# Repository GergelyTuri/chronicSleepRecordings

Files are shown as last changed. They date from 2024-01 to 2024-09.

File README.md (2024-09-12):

# This repository contains hardware and software requirements for running continuous EEG/EMG recordings in mice.

We are developing a EEG/EMG setup to investigate the sleep profile and seizure
incidence in mice using Pinnacle Technology's [3-Channel EEG/EMG Mouse System](https://store.pinnaclet.com/products/8200-k1-3-channel-eeg-emg-mouse-system).

### Table of contents

| **Section** | **Description** |
|:-|:-|
| [Hardware](#hardware) | Hardware requirements and setup tutorial |
| [Software](#software) | Software requirements and setup tutorial |
| [Future directions](#future-directions) | Planned updates to the project |
| [Contact](#contact) | Email the researchers taking lead on the project |

## Hardware

The mouse EEG/EMG experiments take place inside modified Med Associates
sound-attenuating cubicles that are outfitted with
Faraday-shielding copper mesh and sound-proof acoustic foam panels. The
mice undergoing recordings are individually housed inside custom-cut acrylic cages.
Circadian lighting is achieved using LED & IR lights that are powered via
24-hour programmable outlet timers. EEG/EMG signals are recorded
using Pinnacle's EEG/EMG tethered mouse system and headmounts. Overhead cameras are used to record video of
mouse behavior in-sync with EEG/EMG recordings.

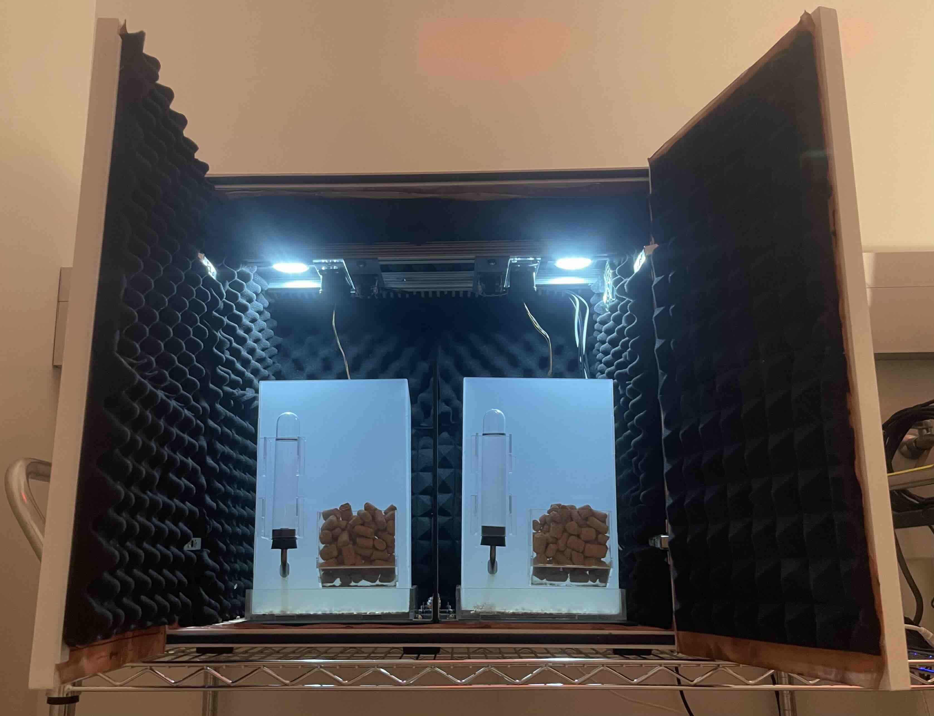
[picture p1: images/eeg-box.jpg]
EEG/EMG cubicle outfitted with copper mesh and acoustic foam panels

**Figure 1.** _Modified cubicle used for EEG/EMG recordings._

### Hardware requirements

- Pinnacle 3-Channel EEG/EMG Mouse System
- Pinnacle EEG/EMG headmounts
- Modified Med Associates Sound Attenuating Cubicle
- Recording enclosure
- Camera(s)
- Desktop/laptop (Windows OS)

### Hardware setup tutorial

For a detailed hardware setup tutorial, please click [here](./Hardware/).

## Software

We are using Pinnacle Technology's [Sirenia Acquisition Software](https://www.pinnaclet.com/sirenia.html) for video-EEG/EMG recordings, which requires the Windows OS environment.

For analysis, we are using [this MATLAB script found here](https://github.com/thepenglab/edfEEG2024) to analyze the sleep states from EEG/EMG data ('.edf' format).

### Software requirement

- [Sirenia Acquisition](https://www.pinnaclet.com/sirenia-download.html)
- [ffmpeg](https://www.gyan.dev/ffmpeg/builds/)
- [MATLAB script](https://github.com/thepenglab/edfEEG2024)
- Windows OS

### Software setup tutorial

For a detailed software setup tutorial, please click [here](./Software/).

## Future directions

1. Developing a software analysis guide
2. Developing a custom analysis code
3. Developing a DeepLabCut model for XY tracking

-----

## Contact

For any questions or inquiries, please email the researchers taking
lead on the project below:
- [Gergely Turi](mailto:gt2253@cumc.columbia.edu)
- [Rebecca Muhle](mailto:ram76@cumc.columbia.edu)
- [David Rivas](mailto:dfr5108@gmail.com)

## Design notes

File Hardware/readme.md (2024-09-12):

# Hardware 

## Hardware requirements

- Pinnacle 3-Channel EEG/EMG Mouse System
- Pinnacle EEG/EMG headmounts
- Modified Med Associates Sound Attenuating Cubicle
- Recording enclosure
- Camera(s)
- Desktop/laptop

## Bill of Materials

For a comprehensive list of hardware materials used in the build, please
click [here](./BOM.md).

## Laser-cut files

For the laser-cut files and drawings, please click [here](./Laser%20cut%20parts/).

## Setup guide

1. [Faraday-shielding and sound-proofing](./setup-guide/copper-foam.md)
2. [Aluminum framing](./setup-guide/aluminum-framing.md)
3. [Pinnacle System, lighting, & ventilation](./setup-guide/pinnacle-system.md)
4. [Camera setup](./setup-guide/camera-setup.md)
5. [Cable management](./setup-guide/cable-management.md)
6. [Recording enclosure](./setup-guide/recording-enclosure.md)
7. [Box divider](./setup-guide/box-divider.md)
8. [Connecting the EEG/EMG headmount](./setup-guide/headmount.md)

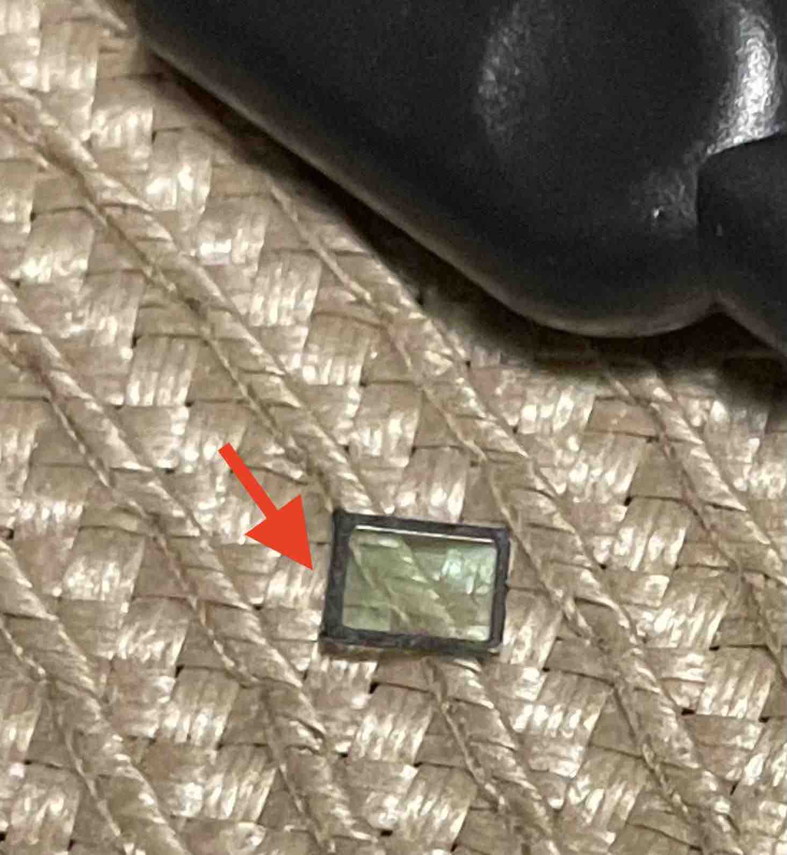
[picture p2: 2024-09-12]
images/logitech-ir-filter.jpg

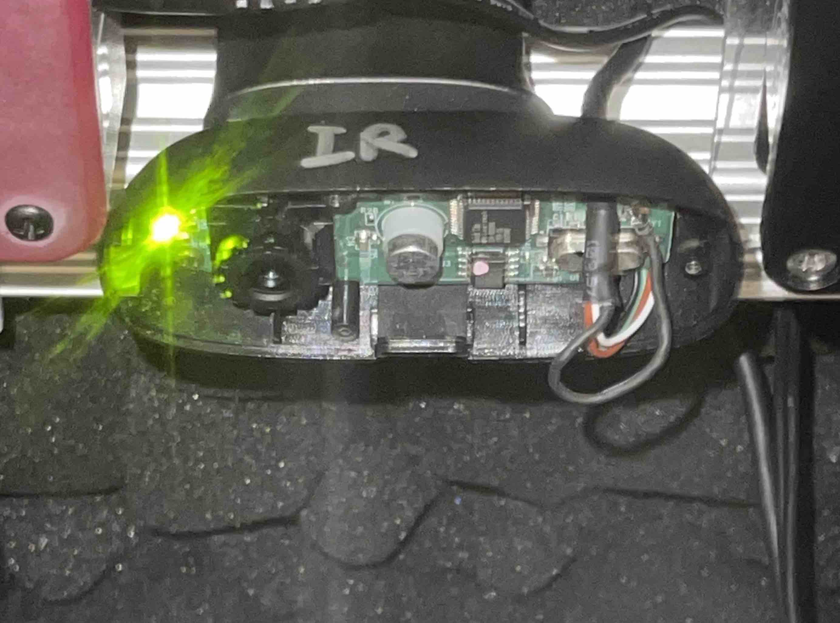
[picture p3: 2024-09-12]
images/logitech-c270.jpg

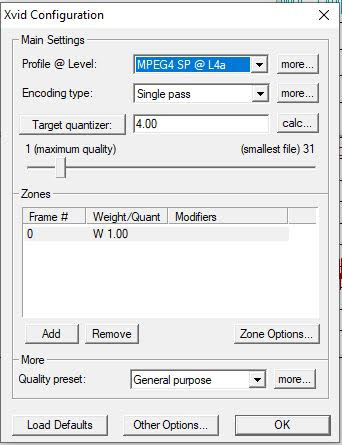
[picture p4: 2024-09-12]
images/xvid-config.jpg

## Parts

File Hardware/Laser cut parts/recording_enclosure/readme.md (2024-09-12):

# Recording enclosure files for laser cutting

The design of the enclosure is based on the Peng lab's*. A small modification has been made in the enclusure so there is no gap between the base and the top. At least two 18"x24", 1/8" thick Frosted Satin Ice acrilyc sheet is needed for the top of one enclosure. One sheet from the 1/4" acrylic is enough to make two bottoms.

* *The original Peng lab design allows the user for using the Peng lab's custom made treadmill for sleep deprivation (it has a gap betwen the bottom and the top).

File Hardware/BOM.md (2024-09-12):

# Bill of Materials

Comprehensive table of the hardware materials used in the build.

| Part name | Source | cat# | function | notes |
| -------- | -------- | -------- | -------- | -------- |
| 3-Channel EEG/EMG Mouse Data Conditioning and Acquisition System | Pinnacle Tech. | [8206-HR](https://store.pinnaclet.com/collections/3-channel-tethered-mouse-systems/products/8200-k1-3-channel-eeg-emg-mouse-system) | 2 EEG/ 1 EMG amplifier | |
| 3 channel mouse preamplifier | Pinnacle Tech. | [8202](https://store.pinnaclet.com/products/8202-3-channel-mouse-preamplifier) | Connects headmount to commutator | Custom length of 11.25 inches from connector to connector |
| 3-Channel Mouse Commutator and Swivel (6-pin) | Pinnacle Tech. | [8204-723](https://store.pinnaclet.com/products/8204-723-3-channel-mouse-commutator-and-swivel-6-pin) | Commutator ||
| 2 EEG/1 EMG Mouse Headmount | Pinnacle Tech. | [8201-SS](https://store.pinnaclet.com/products/8201-2-eeg-1-emg-mouse-headmount?variant=12390701727847) | EEG/EMG electrodes that connect to the 6-pin preamplifier | |
| 6 PIN Male to Male Cable (6 ft.) | Amazon | [B0933GL5CX](https://www.amazon.com/Shielded-Cable-Black-Mouse-Keyboard/dp/B0933GL5CX/) | Extension cable between 8206 amplifier and commutator |
| EEG/EMG Headmounts | Pinnacle Tech. | [8201-SS](https://store.pinnaclet.com/products/8201-2-eeg-1-emg-mouse-headmount?variant=12390701727847) | EEG/EMG signal probe | |
| Sound Attenuating Cubicle | Med Associates | [MDF](https://med-associates.com/product/sound-attenuating-cubicles-mdf/) | Cubicle enclosure | |
| Copper mesh (0.0045" diameter) | TWP | [100X100C0045](https://www.twpinc.com/100-mesh-copper-0045-wire-dia) | Faraday-shielding | Fixed using staples |
| Acoustic foam panels | Amazon | [B0BLTSW8KC](https://www.amazon.com/Self-Adhesive-Quick-Recovery-Elasticity-Eco-Friendly-WVOVW/dp/B0BLTSW8KC) | Sound-proofing | Fixed using staples |
| T-slot aluminum extrusion profile framing | 80/20 | [1010](https://8020.net/1010.html) | Mounting overhead accessories | Installed with 1/4" screws |
| Roll-in T-nuts | 80/20 | [3313](https://8020.net/3313.html) | Mounting overhead equipment to aluminum railing | |
| 10 & 15 Series Wiring Duct | 80/20 | [2899](https://8020.net/2899.html) | Cable management | Can alternatively use cable raceway |
| 1/8" & 1/4" acrylic sheets | Canalplastics | [various materials](https://www.canalplastic.com/) | material used for laser cutting | |
| Weld-on #4 glue | Amazon | [B00TCUJ7A8](https://www.amazon.com/Weldon-Applicator-Bottle-Pint-10308/dp/B00TCUJ7A8) | Adhere acrylic sheets | Applied with needle |
| Rat water bottle | WPI | [505432](https://www.wpiinc.com/var-505432-rat-mouse-water-bottle.html) | | |
| Arducam B0205 Camera | Amazon | [B0829HZ3Q7](https://www.amazon.com/Arducam-Computer-Automatic-Switching-All-Day/dp/B0829HZ3Q7/) | Video monitoring | |
| Dimmable LED lights | Amazon | [B0CCDPNYFG](https://www.amazon.com/JUSJUBR-Lighting-Dimmable-Function-Bookshelf/dp/B0CCDPNYFG) | Artificial daylight | |
| LED rotary dimmer switch | Amazon | [B07MM88SB6](https://www.amazon.com/TronicsPros-12V-24V-Dimmer-Switch-Controller/dp/B07MM88SB6) | Change LED light intensity | |
| IR light (optional) | Pinnacle Tech. | [9057](https://store.pinnaclet.com/products/9057-illuminator) | Night-time lighting | The Arducam B0205 camera already has automatic IR light bulbs |
| 24-HR programmable outlet timer | Amazon | [B07HCQKRRY](https://www.amazon.com/Fosmon-Programmable-Seasonal-Portable-Aquarium/dp/B07HCQKRRY) | Program circadian lighting | |
| 12V power sources | Amazon | N/A | powering multiple components | |
| 24V AC-to-DC power supply | Amazon | [B078RY7BPL](https://www.amazon.com/ALITOVE-Converter-Transformer-5-5x2-1mm-Computer/dp/B078RY7BPL) | Powering the cubicle fan | |

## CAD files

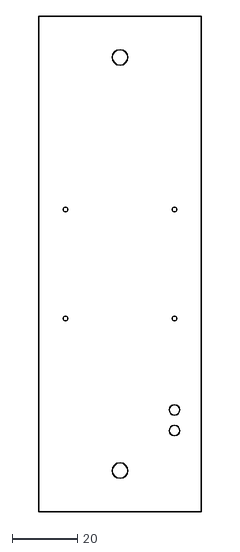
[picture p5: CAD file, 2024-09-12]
Hardware/Laser cut parts/arducam_mount/arducam_camera_mounting_plate.dxf
50.0 x 152.4

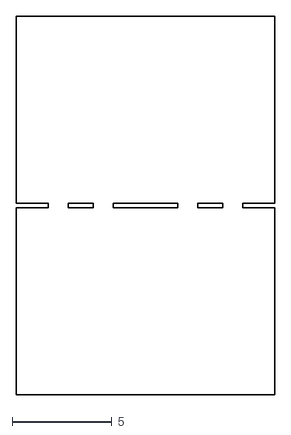
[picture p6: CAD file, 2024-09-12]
Hardware/Laser cut parts/box-divider/box-divider-pt2.dxf
13.0 x 19.0

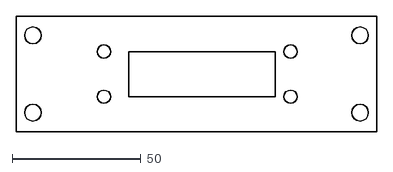
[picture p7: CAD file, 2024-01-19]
Hardware/Laser cut parts/commutator-holder/8206-commutator-holder/commuter holder GTs system.dxf
140.0 x 45.0

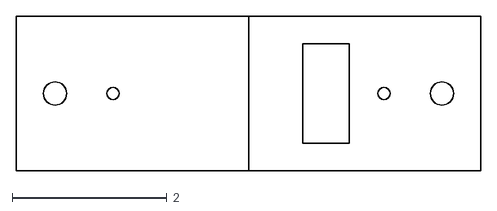
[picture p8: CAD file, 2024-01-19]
Hardware/Laser cut parts/commutator-holder/8401-commutator-holder/Commuter holder RMs system.dxf
6.00 x 2.00

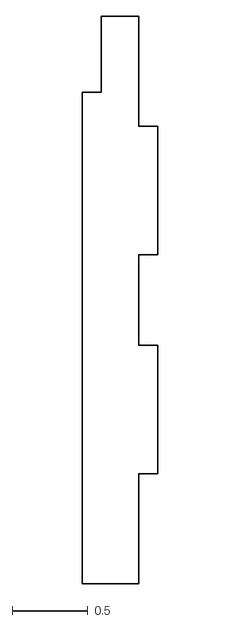
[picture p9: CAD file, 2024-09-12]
Hardware/Laser cut parts/fan-cover/fan-cover-pt2.dxf
0.5 x 3.75

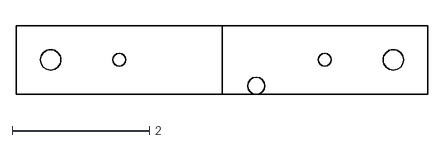
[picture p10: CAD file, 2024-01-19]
Hardware/Laser cut parts/ir_holder/IR_holder.dxf
6.00 x 1.01

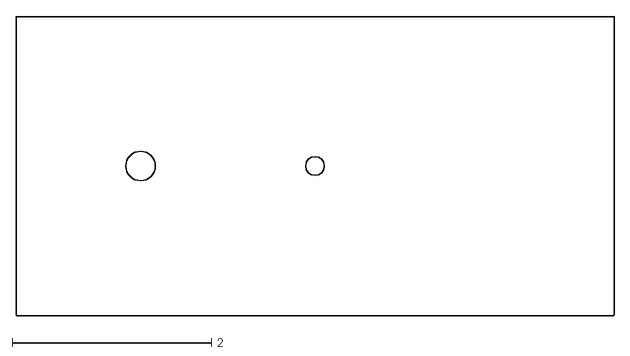
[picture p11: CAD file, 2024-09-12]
Hardware/Laser cut parts/led_mount/led_light_puck_mount.dxf
6.00 x 3.00

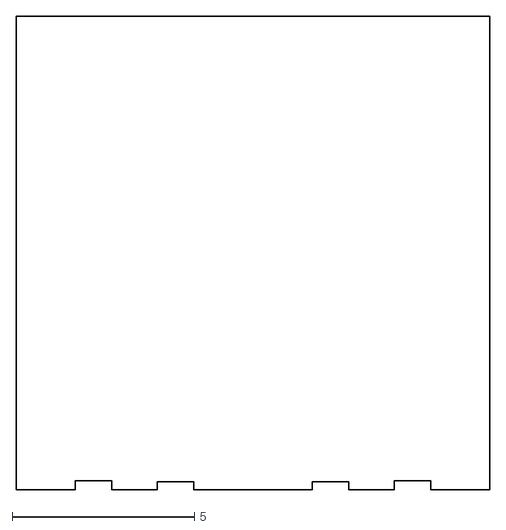
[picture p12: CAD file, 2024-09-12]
Hardware/Laser cut parts/box-divider/box-divider-pt1.dxf
13.0 x 13.0

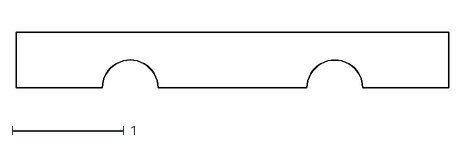
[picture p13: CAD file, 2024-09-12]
Hardware/Laser cut parts/fan-cover/fan-cover-pt3.dxf
3.88 x 0.5

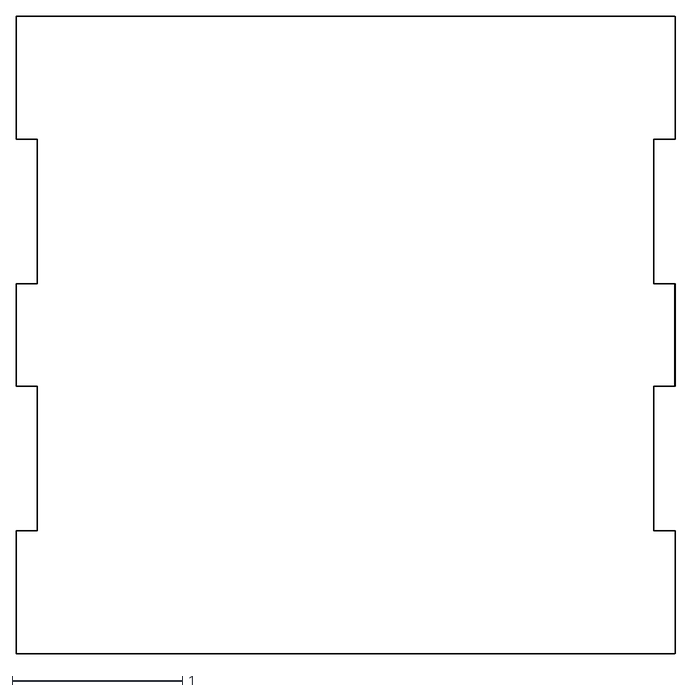
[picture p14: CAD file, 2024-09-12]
Hardware/Laser cut parts/fan-cover/fan-cover-pt1.dxf
3.88 x 3.75

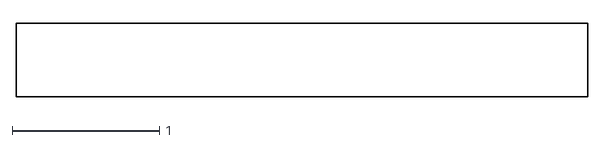
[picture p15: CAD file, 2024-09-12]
Hardware/Laser cut parts/fan-cover/fan-cover-pt4.dxf
3.88 x 0.5

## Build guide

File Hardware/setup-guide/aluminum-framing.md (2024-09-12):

## Aluminum framing

This portion of the guide explains the installation of the aluminum
framing/railing, which is used to mount overhead equipment.

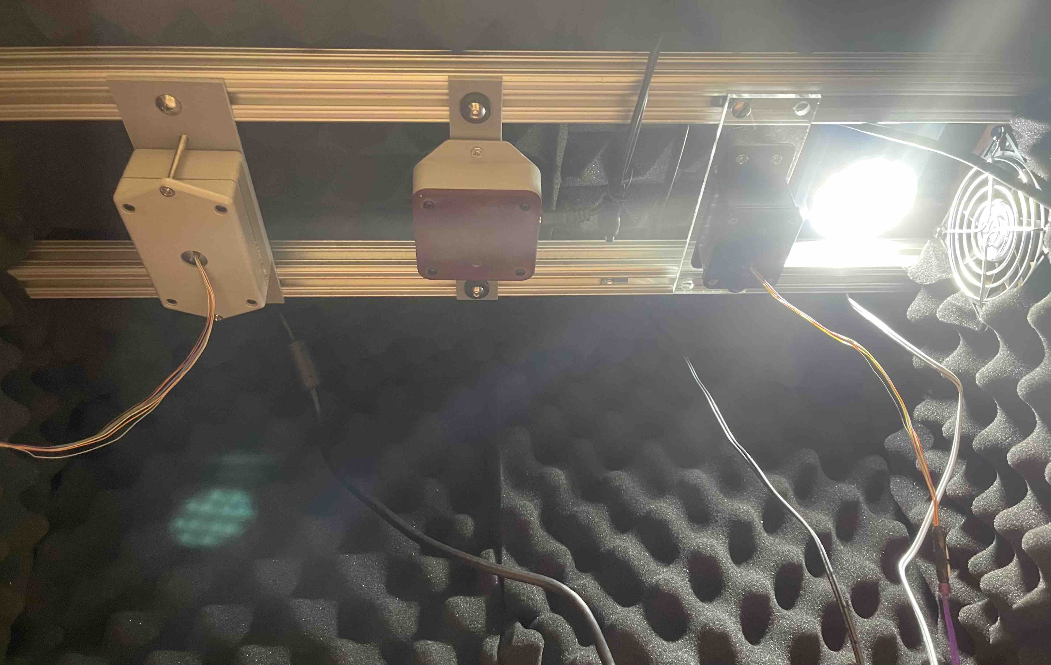
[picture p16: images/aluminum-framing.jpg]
Example of aluminum framing inside Med Associates box

**Figure 1.** _Example of overhead equipment mounted to the aluminum framing._

**Materials**
- [T-slot aluminum extrusion profile framing 1010](https://8020.net/1010.html)
- [T-nuts](https://8020.net/3313.html)
- 1/4" screws
- Drill

**Steps**
1. Install two aluminum railings (23 3/8" long) that are positioned 1.5" from
   the ceiling and 5" apart using 1/4" screws and a drill
    * Using a blade, carefully remove four square pieces of acoustic foam from the inside wall of
      the box corresponding to the cross-sectional width of the aluminum railings
    * Drill the screws, starting from the outside surface of the box
2. After installing the railings, roll in T-nuts to the railing's T-slots to
   your liking, which can be used to fix overhead attachments

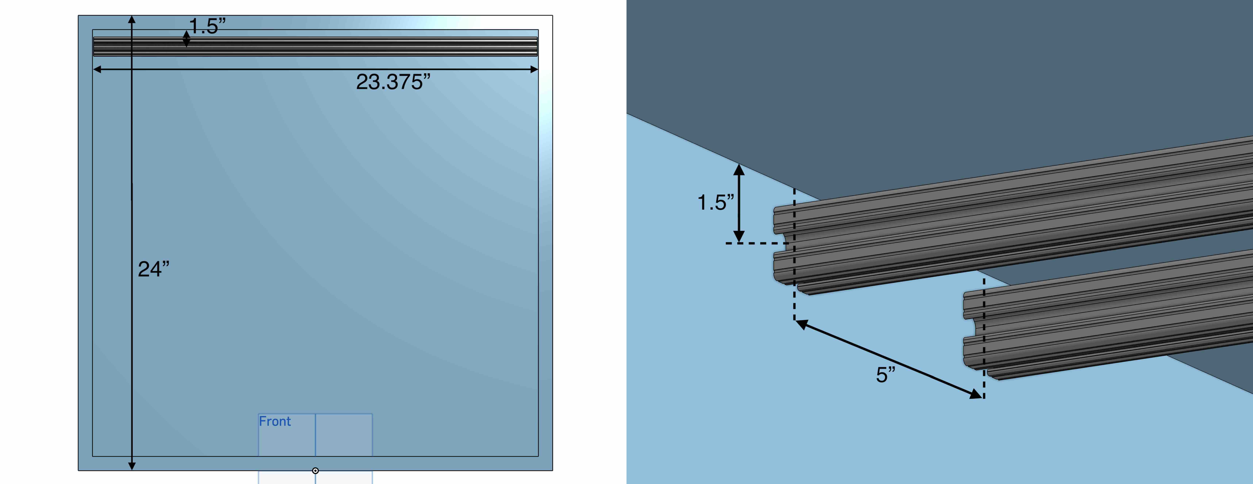
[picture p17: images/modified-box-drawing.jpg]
Drawing of aluminum framing inside Med Associates box

**Figure 2.** _Drawing of aluminum framing inside Med Associates box._

[← Return to setup guide](../readme.md#setup-guide)

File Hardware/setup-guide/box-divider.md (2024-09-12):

## Box Divider

The box divider will separate the two recording enclosures from one another. For optimal sturdiness and durability, 1/4" thick acrylic is recommended, but 1/8" could be used alternatively.

**Materials**
- [1/4" black matte acrylic sheets](https://www.canalplastic.com/products/2025-black-opaque-p95-acrylic-sheet)
- [L-brackets]()
- Drill 
- [Screws]()
- [Washers]()
- Laser cutter ([Thunder Laser Nova
  35](https://www.thunderlaserusa.com/machines/nova/) used)

**Steps**
1. Laser-cut 1/4" black matte acrylic sheets using the laser-cut files [found here](.././Laser%20cut%20parts/arducam_mount)
2. Drill six holes in the acrylic sheets
3. Fit the two sheets parallel to one another
4. Align six L-brackets with the drilled holes, then fix the brackets into place using the screws, washers, and nut bolts
5. Place the assembled box divider inside of the Med Associates box, and place the recording enclosures on-top of the divider

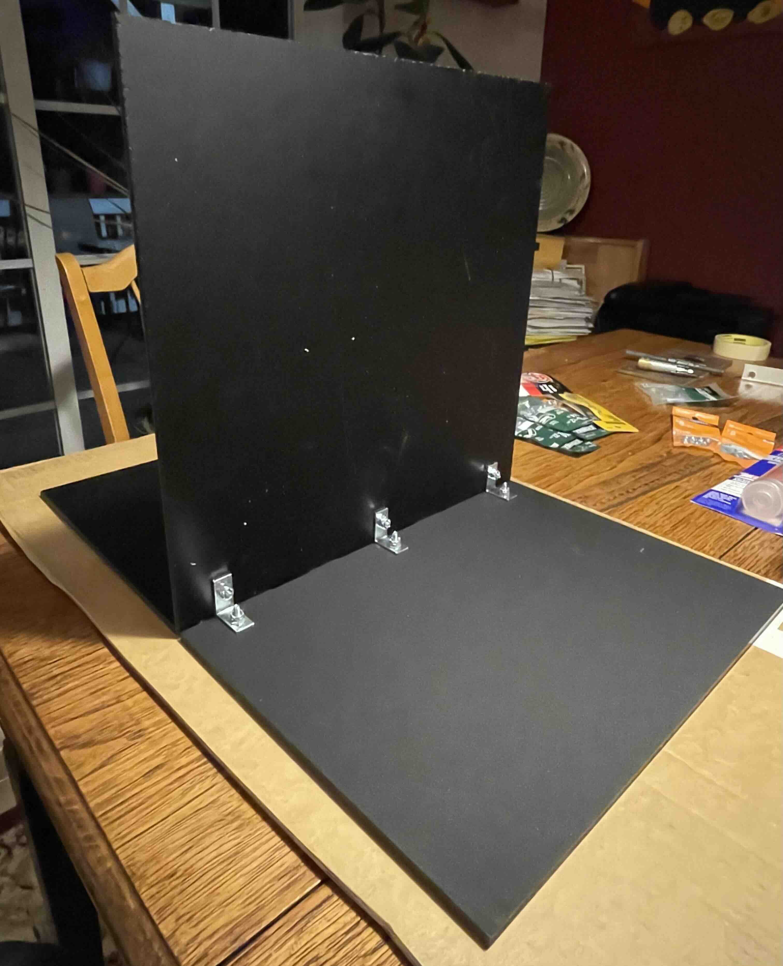
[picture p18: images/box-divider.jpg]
Assembled box divider

**Figure 1.** _Assembled box divider._

[← Return to setup guide](../readme.md#setup-guide)

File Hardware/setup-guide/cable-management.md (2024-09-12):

## Cable management

This portion of the guide details the cable management inside of the Med
Associates box, which gives it a professional and aesthetically-pleasing look.

We are using a wiring duct from 80/20 that's designed for 10 series aluminum
framing, but a generic [1" cable raceway](https://www.amazon.com/dp/B0BX69L3L2) can be used alternatively.

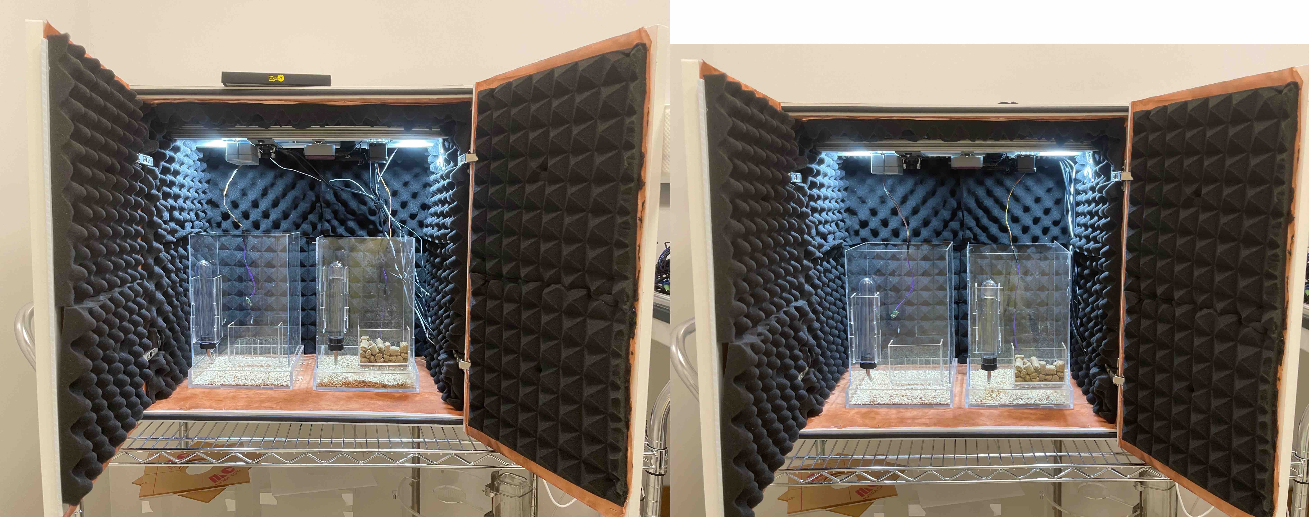
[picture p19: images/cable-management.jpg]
Before and after cable management inside modified Med Associates box

**Figure 1.** _Before and after cable management inside of the modified Med Associates box._

**Materials**
- [10 & 15 Series Wiring Duct](https://8020.net/2899.html)
- [T-nuts](https://8020.net/3313.html) & screws
- Velcro cable ties

**Steps**
1. Roll in at least four T-nuts to the backside of the aluminum frame that is
   closest to the back wall
2. Using screws, fix the wiring duct to the T-nuts
    * It is easier to install the screws by cutting the teeth of the wiring duct that neighbor each T-nut
3. Feed the wires through the wiring duct and out to the cable hole found on the side
   of the Med Associates box
4. Bundle and tie the exposed cables together with a velcro cable tie. Attach the
   velcro to the acoustic foam.

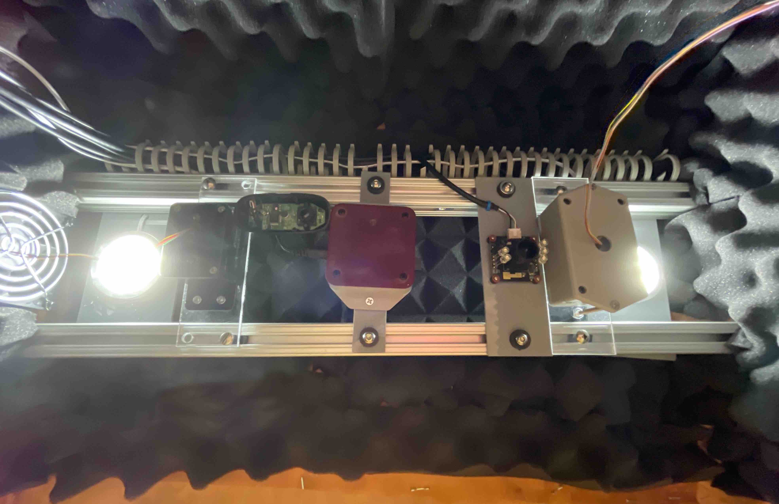
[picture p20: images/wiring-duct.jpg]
Wiring duct installed inside of Med Associates box

**Figure 2.** _Wiring duct installed inside of modified Med Associates box._

[← Return to setup guide](../readme.md#setup-guide)

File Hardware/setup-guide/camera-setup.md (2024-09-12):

## Camera setup

This portion of the guide explains the camera modifications and setup. This will
enable the ability to record continuous video in LED- and IR-lit conditions.

We are currently using two different cameras, each of which have their own setup
instructions below.

**Materials**
- [Arducam B0205 camera](https://www.amazon.com/Arducam-Computer-Automatic-Switching-All-Day/dp/B0829HZ3Q7/)
- [Arducam plate mount](./Laser%20cut%20parts/arducam_mount)
- [1/8" acrylic sheets](https://www.canalplastic.com/)
- Laser cutter ([Thunder Laser Nova
  35](https://www.thunderlaserusa.com/machines/nova/) used)
- [T-nuts](https://8020.net/3313.html) & screws
- Small plastic zip ties

### Arducam B0205 camera setup

**Steps**
1. Laser-cut the plate mount for the Arducam using acrylic sheets and the
   laser-cut file [found here](.././Laser%20cut%20parts/arducam_mount)
2. Fix the camera to the plate mount and T-nuts using screws
3. Secure the usb cable to the plate using a zip tie
4. Feed the wire through the cable hole found on the side of the Med Associates
   box

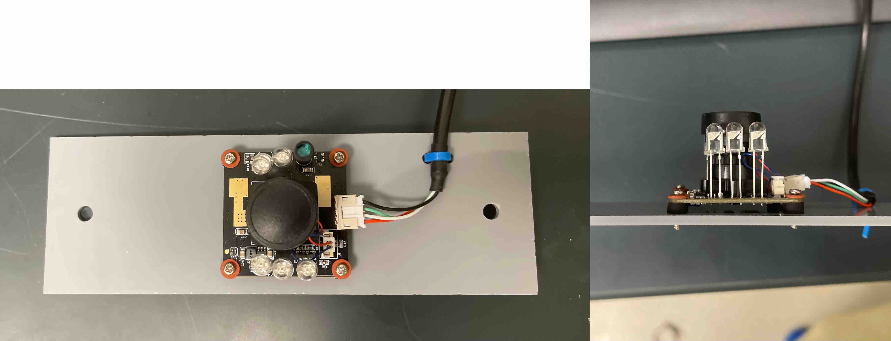
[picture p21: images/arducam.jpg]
Arducam B0205 secured to mounting plate

**Figure 1.** _Arducam B0205 secured to mounting plate._

[← Return to setup guide](../readme.md#setup-guide)

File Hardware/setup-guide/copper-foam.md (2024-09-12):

## Faraday-shielding and sound-proofing

This portion of the guide explains the Faraday-shielding and sound-proofing of
the Med Associates box, which reduces external electromagnetic fields and noise.
This will serve as a controlled environment for the EEG/EMG recordings to take
place.

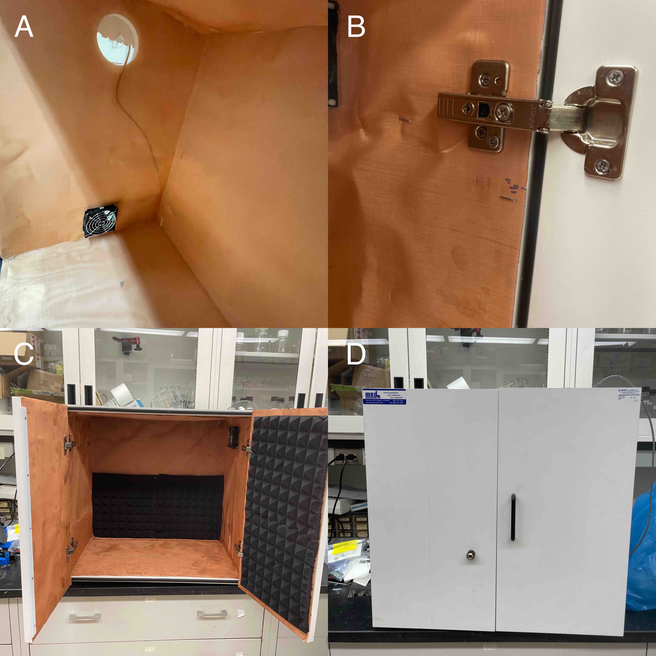
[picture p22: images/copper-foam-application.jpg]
Photo collage showcasing the installation of copper mesh and acoustic foam panels

**Figure 1.** _Sequential application of copper mesh and acoustic foam panels._
(A & B) Installation of the copper mesh. (C) Installation of the acoustic foam
panels. (D) Outside view of the newly modified box.

**Materials**
- [Med Associates Sound Attenuating Box](https://med-associates.com/product/sound-attenuating-cubicles-mdf/)
- [Copper mesh](https://www.twpinc.com/100-mesh-copper-0045-wire-dia)
- [Acoustic foam panels](https://www.amazon.com/Self-Adhesive-Quick-Recovery-Elasticity-Eco-Friendly-WVOVW/dp/B0BLTSW8KC)
- Staples & staple gun
- Disinfecting wipes

**Steps**
1. Clean the inside of the Med Associates box with disinfecting wipes
2. Uninstall the doors from the hinges
3. Measure and cut the copper mesh to the dimensions of the inside box and door
   panels
4. Fix the copper mesh to the inside box surfaces with staples
5. Cut holes in the copper mesh for the box's door hinges, ventilation fan, and cable hole
6. Reinstall the screws for the door hinges through the copper mesh
7. Fix the acoustic foam panels, over the copper mesh, to the inside box
   surfaces with staples
8. Cut holes in the foam for the door hinges, ventilation fan, and cable hole

[← Return to setup guide](../readme.md#setup-guide)

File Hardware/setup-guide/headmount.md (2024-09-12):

## Connecting the EEG/EMG headmount

This portion of the guide explains how to properly connect the preamplifier to
the EEG/EMG headmount. We are using isoflurane to anesthetize the mice during the
connection of the preamplifier to the headmount.

**Materials**
- [2 EEG/1 EMG Mouse Headmount](https://store.pinnaclet.com/products/8201-2-eeg-1-emg-mouse-headmount?variant=12390701727847)
- [3 channel mouse preamplifier](https://store.pinnaclet.com/products/8202-3-channel-mouse-preamplifier)
- Isoflurane and paper towels
- Tupperware container with lid
- Hemostat

**Steps**
1. Apply a small amount of isoflurane to a piece of paper towel
2. Place this paper towel into a tupperware container
3. Transfer a mouse into the tupperware container and secure the lid
    * Wait 1-2 minutes for the isoflurane to take effect
4. Transfer the mouse from the tupperware container to the cage floor of the recording enclosure
5. Carefully insert the 6-pin male connector of the preamplifier into the
   headmount
    * **IMPORTANT**: There are two black squares on one side of the preamplifier and one black
      square on the opposite side. The side with **two** black squares is the
      **posterior**, whereas the side with **one** black square is the **anterior**.
    * Use a hemostat to carefully hold the headmount in place
    * Be very gentle with the mouse while inserting the preamplifier pins to the headmount
    
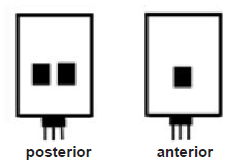
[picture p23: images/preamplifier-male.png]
Posterior and anterior sides of the 6-pin preamplifier male connector
    
    
    **Figure 1.** _Posterior and anterior sides of the 6-pin preamplifier male connector._

6. Carefully place the mouse inside of the recording enclosure
7. Allow sufficient time to pass for the mouse to recover from the anesthesia
   before proceeding with an experiment

[← Return to the setup guide](../readme.md#setup-guide)

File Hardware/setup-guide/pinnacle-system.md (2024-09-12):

## Pinnacle System, lighting, & ventilation

This portion of the guide explains how to setup the Pinnacle System, circadian
lighting, and ventilation. This is the key hardware of the EEG/EMG recording setup.

**Materials**
- Pinnacle Data Conditioning and Acquisition System(s) (Models [8206](https://store.pinnaclet.com/products/8206-data-conditioning-and-acquisition-system) used)
- Amplifier-to-commutator extension cables ([8206
  extension](https://www.amazon.com/Shielded-Cable-Black-Mouse-Keyboard/dp/B0933GL5CX/)
  used)
- [LED
  lights](https://www.amazon.com/JUSJUBR-Lighting-Dimmable-Function-Bookshelf/dp/B0CCDPNYFG)
- [LED rotary dimmer
  switch](https://www.amazon.com/TronicsPros-12V-24V-Dimmer-Switch-Controller/dp/B07MM88SB6)
- Light meter
- [24-HR programmable outlet
  timer](https://www.amazon.com/Fosmon-Programmable-Seasonal-Portable-Aquarium/dp/B07HCQKRRY)
- [24V AC-to-DC power supply](https://www.amazon.com/ALITOVE-Converter-Transformer-5-5x2-1mm-Computer/dp/B078RY7BPL)
- Custom laser-cut parts (refer to [laser cut
  files](.././Laser%20cut%20parts/))
- [1/8" acrylic sheets](https://www.canalplastic.com/)
- Laser cutter ([Thunder Laser Nova
  35](https://www.thunderlaserusa.com/machines/nova/) used)
- [Weld-on #4
  glue](https://www.amazon.com/Weldon-Applicator-Bottle-Pint-10308/dp/B00TCUJ7A8)
- [T-nuts](https://8020.net/3313.html) & screws

**Before starting**
1. Laser-cut the acrylic parts for the commutators, LED lights, and fan cover using acrylic sheets and the laser-cut files [found here](.././Laser%20cut%20parts/)

### Pinnacle System setup
1. Laser cut the commutator plate mount using clear acrylic (1/8" thick)
2. Fix the commutator(s) to the plate mounts using screws
3. Then, fix these plate mounts to the aluminum framing using T-nuts
4. Install the amplifier-to-commutator extension cables
5. Ensure the commutator is mounted directly overhead the intended spot for the recording enclosure
6. Feed the wires through the cable hole found on the side of the Med Associates box

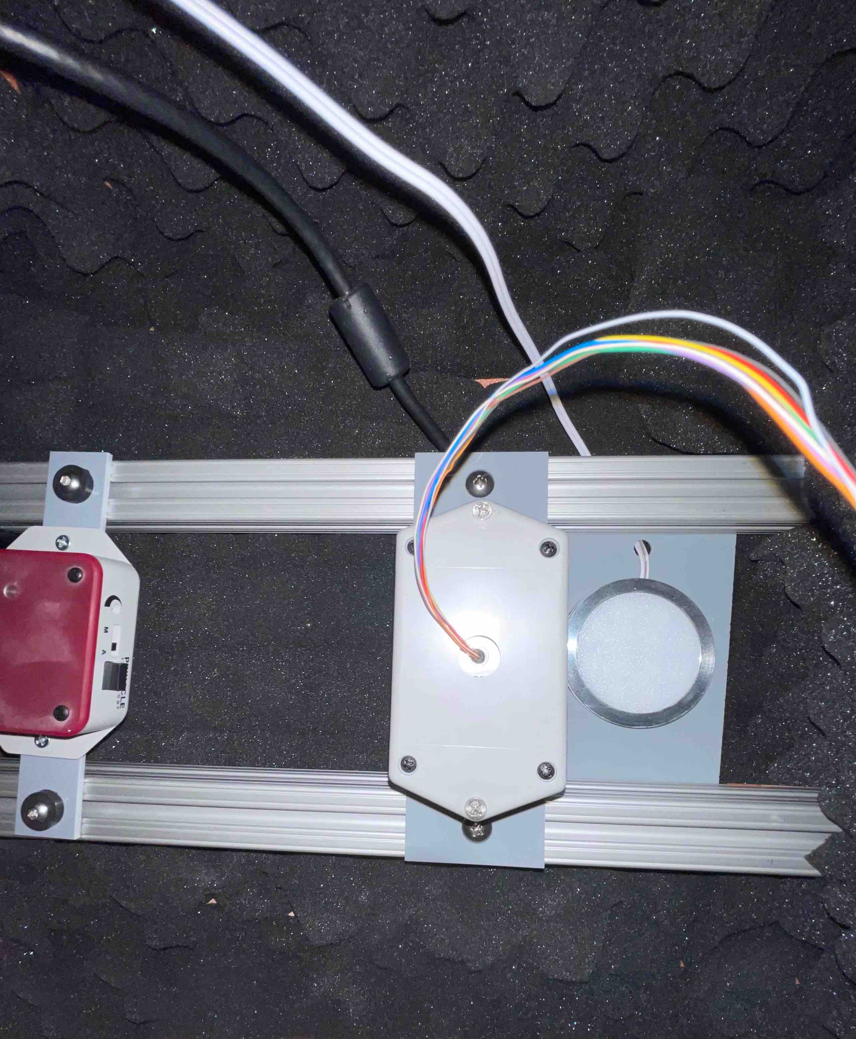
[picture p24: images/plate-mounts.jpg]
Example of mounting plates fixed to aluminum framing

**Figure 1.** _Mounting plates fixed to aluminum framing._

### Lighting setup 
1. Laser cut the LED light plate mounts using opaque acrylic (1/8" thick)
2. Fix the LED light pucks to the center of the plate mounts using screws
  * Feed the LED light cables through the outer hole of the plate mount
3. Slide the LED lights, now fixed to their mounting plates, between the top of the aluminum framing and the ceiling
4. Feed the wires through the cable hole found on the side of the Med Associates box
5. Replace the manufacturer's LED light dimmer switch with the rotary dimmer switch
6. Place a light meter inside the box, close the doors, and dial the rotary dimmer to the desired LED light intensity
  * Our box's light intensity is set to **90 lux**
  * After determining the desired light intensity, mark a line on the rotary with a permanent marker
7. Connect the LED light power cable directly to a 24-HR programmable outlet timer
  * Program the timer "on" phase to be 12 hours

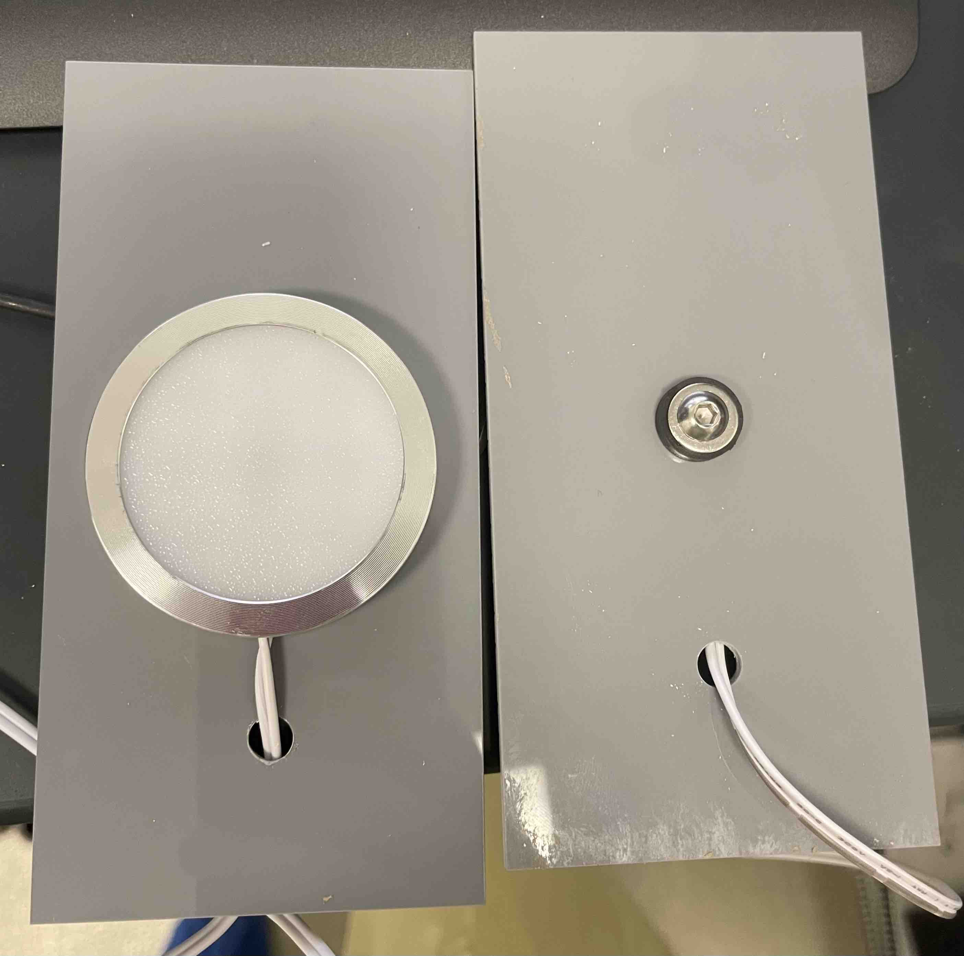
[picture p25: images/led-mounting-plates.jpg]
LED pucks fixed to mounting plates

**Figure 2.** _LED pucks fixed to mounting plates._

### Ventilation setup
1. Laser cut the acrylic fan cover parts using opaque acrylic (1/8" thick) 
2. Assemble and glue the fan cover parts with Weld-On #4
  * Allow to air dry overnight
3. Slide the fan cover over the ventilation fan outside of the box
4. Connect the 24V AC-to-DC power supply to the ventilation fan

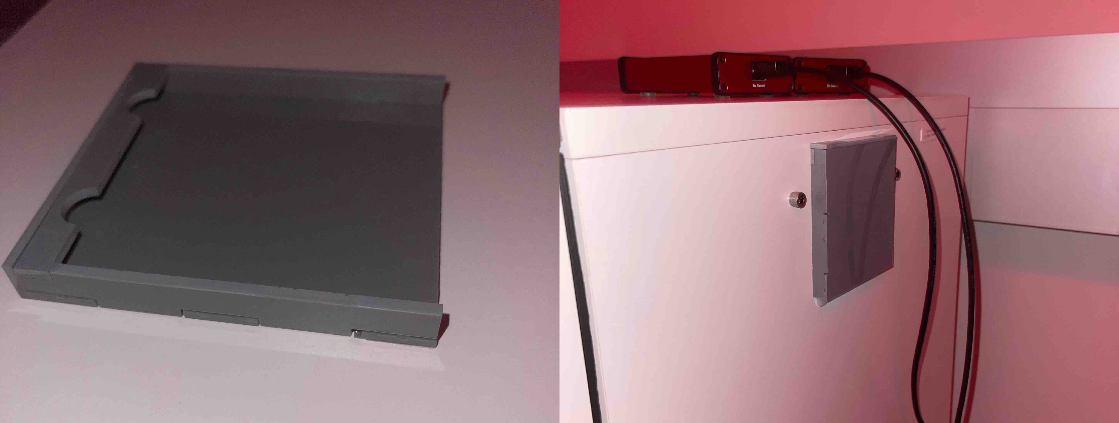
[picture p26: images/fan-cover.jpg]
Fan cover placed over ventilation fan

**Figure 3.** _Assembled fan cover (left). Fan cover placed over top of ventilation fan (right)._

[← Return to setup guide](../readme.md#setup-guide)

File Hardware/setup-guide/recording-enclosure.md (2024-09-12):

## Recording enclosure

The recording enclosure will house the mice undergoing EEG/EMG recordings. These
enclosures should be outfitted with food and water supply compartments.

We are using recording enclosures designed by [Dr. Yueqing
Peng](https://www.pathology.columbia.edu/profile/yueqing-peng-phd). These are
made of clear-acrylic sheets that are adhered together using Weld-on #4 glue.
Please contact Dr. Peng for the laser-cut files.

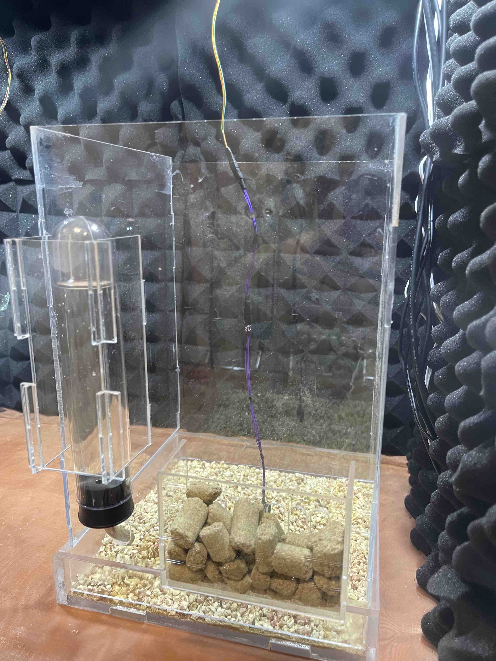
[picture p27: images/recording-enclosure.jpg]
Recording enclosure made of acrylic sheets

**Figure 1.** _Recording enclosure designed by Dr. Yueqing Peng._

**Materials**
- [Rat water
  bottles](https://www.wpiinc.com/var-505432-rat-mouse-water-bottle.html)
- [1/8" & 1/4" frosted satin ice acrylic sheets](https://www.canalplastic.com/products/0d010-df-frosted-satin-ice-acrylic-sheet)
- [Weld-on #4
  glue](https://www.amazon.com/Weldon-Applicator-Bottle-Pint-10308/dp/B00TCUJ7A8)
- Corner clamps & lab tape
- Laser cutter ([Thunder Laser Nova
  35](https://www.thunderlaserusa.com/machines/nova/) used)

**Steps**
1. Laser-cut frosted stain ice acrylic sheets (1/8" & 1/4" thick)
2. Use corner clamps and lab tape to hold acrylic sheets together firmly
3. Using the applicator bottle with a syringe needle tip (sold with Weld-on #4),
   hold the bottle upright and gently squeeze air out, then release this pressure while simultaneously flipping the bottle upside down
    * This will remove any air bubbles during the glue application
4. Place the needle at the bottom corner between the two acrylic sheets and
   apply a small amount of glue from the bottom to top
    * The glue will absorb between the sheets via capillary action and the
      space between the acrylic sheets will appear wet
    * Be careful to allow any excess glue on the acrylic surface to air dry, as touching the glue can
      leave a visible mark
    * Glue residue that is visible on the surface after drying can be removed with polish
      compound and a cloth
5. Wait 3-5 minutes to allow the glued acrylic sheets to harden
    * During this time, apply firm pressure to any points between the acrylic sheets that have visible air pockets
6. Remove the corner clamps and continue gluing additional acrylic sheets together
7. After 24 hours of air drying, remove any lab tape from the assembly
8. Ensure the recording enclosure is placed inside the Med Associates box
   centered directly underneath the commutator and preamplifier

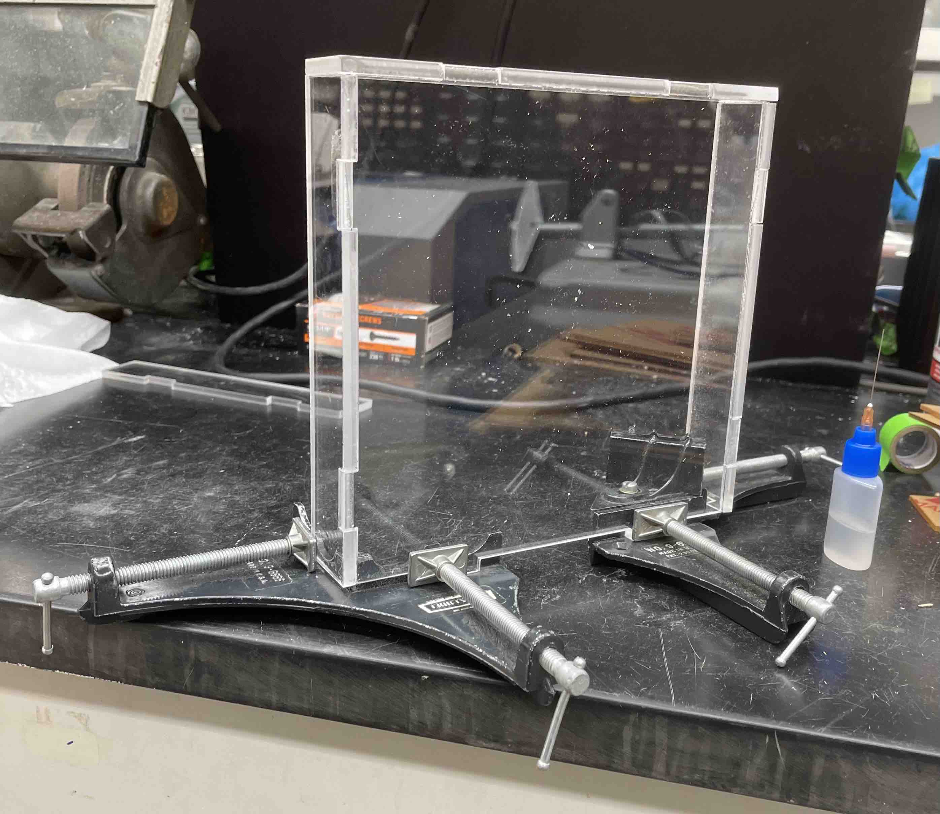
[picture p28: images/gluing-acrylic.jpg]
Using corner clamps to hold acrylic together while gluing

**Figure 2.** _Using corner clamps to hold acrylic sheets together during the glue application._

Alternatively, you can [purchase a cage from Pinnacle
Technology](https://store.pinnaclet.com/collections/cages).

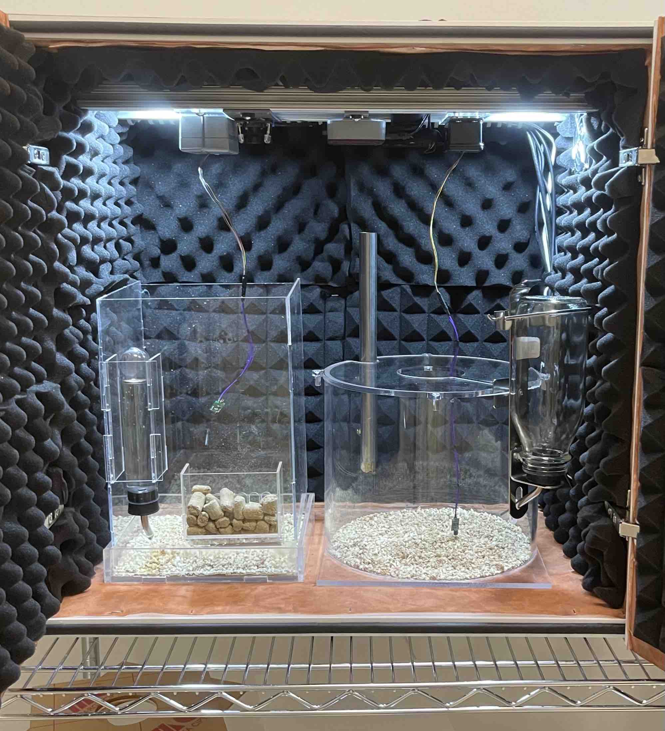
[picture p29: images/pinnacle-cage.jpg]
Recording enclosures made of acrylic

**Figure 3.** _Side-by-side comparison of the cage designed by Dr. Yueqing Peng
(left) and Pinnacle Technology (right; Cat. <a
href="https://store.pinnaclet.com/collections/cages/products/8228-mouse-cage">8228</a>)._

[← Return to setup guide](../readme.md#setup-guide)

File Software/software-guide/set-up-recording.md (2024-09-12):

## Setting up an EEG/EMG recording

This portion of the guide explains how to begin recording a video-EEG experiment
in Sirenia Acquisition. By default, Sirenia Acquisition experiments save in the `.pvfs` format. More than one amplifier and camera can be recorded at once in a single project file. Each amplifier will record EEG/EMG signal from the mouse it's connected to.

The EEG/EMG headmount should already be connected to the preamplifier before
beginning this portion of the guide. For instructions on how to properly connect
the headmount, please click [here](../../Hardware/setup-guide/headmount.md).

**Software required**
- [Sirenia Acquisition](https://www.pinnaclet.com/sirenia-download.html)
- Windows OS

**Steps**
1. In the top toolbar, select 'File > New Experiment'. A new window will appear.
    1. In the 'File:' prompt, choose a folder destination and file name
        * In our setup, we save project files to: 'E:/Sirenia-Acquisition-Experiments/[lab name]/'
    2. Enter the experiment name and animal ID in their respective fields
    3. Click 'Add Device' (USB icon). A small pop-up named 'Select Pod Device' will appear.
        * Under 'Connection', choose the amplifier system you will be using. The window will automatically close after selecting an amplifier.
          * **'8206HR - 21342'**: The amplifier on the left-side of our box (check labels on top of box)
          * **'8206HR-SL - 20275'**: The amplifier on the right-side of our box (check labels on top of box)
2. In the top menu, click 'Add Camera' (webcam icon) to add a camera source
    * Type: 'Box/Dome/USB Camera'
    * Camera: USB Camera 6369
      * By default, the Arducam B0205 camera is named 'USB Camera 6369'. Note how in our setup, there are two cameras listed with this same name.
3. Below the top menu are various tabs such as 'Device Params', 'EEG/EMG
   Channels', and 'Info', alongside tabs corresponding to the name of the amplifier
   and camera used
    * In the 'Info' tab, edits can be made to the project name, file name,
      Animal ID, etc.
4. Check the EEG/EMG signals and video feed to ensure the hardware is working as
   intended
    * If needed, adjust the position of the recording enclosure so that it's
      centered in the video frame
5. In the top menu, click the record button (round red button with letter 'R') to start recording the experiment
6. At the end of the experiment, click the red 'X' icon in the top menu to close experiment

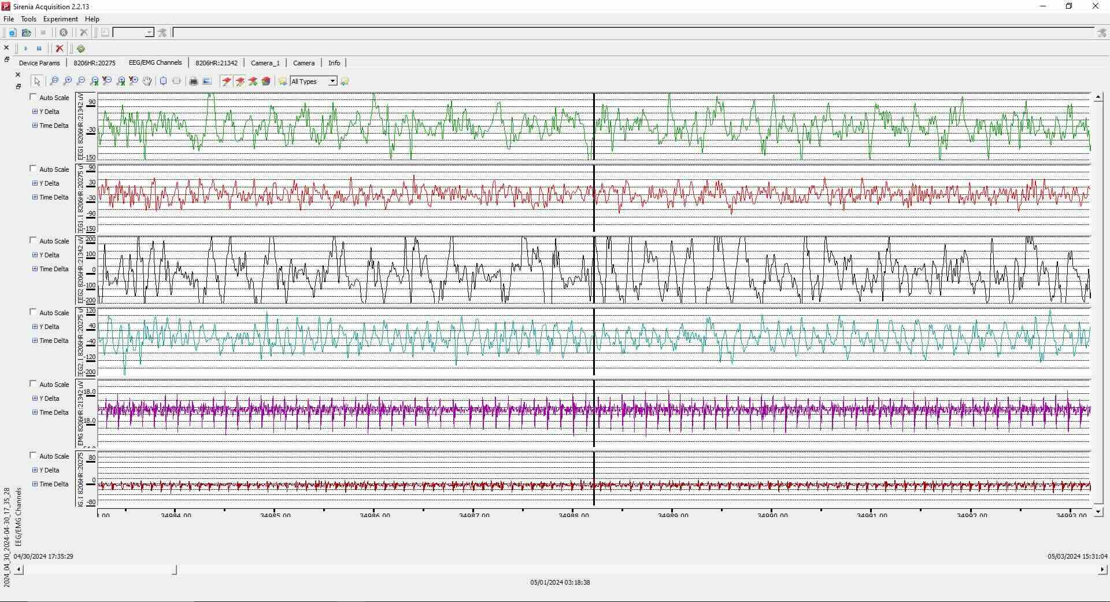
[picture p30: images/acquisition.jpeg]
EEG/EMG recording in Sirenia acquisition

**Figure 1.** _EEG/EMG recording in Sirenia acquisition._

[← Return to setup guide](../readme.md#setup-guide)

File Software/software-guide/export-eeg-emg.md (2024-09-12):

## Exporting the EEG/EMG channels

This portion of the guide explains how to export a video-EEG experiment in Sirenia Acquisition. EEG/EMG data can be exported to an `.edf` format, which can then be analyzed using the MATLAB script, Sirenia software packages, or third-party software.

**Software required**
- [Sirenia Acquisition](https://www.pinnaclet.com/sirenia-download.html)
- Windows OS

By default, the project files are in `.pvfs` format, which are located in
the folder destination that was selected in the 'File:' prompt during the
project setup. This filetype will store project info, EEG/EMG data, and video. Additionally, this format can be opened with Sirenia software packagages, which in that case it's not necessary to export data to a different file format.

If you plan to analyze the channels using the MATLAB script, it's
required you export data in the `.edf` format:

**Steps**
1. In the top toolbar, select 'File > Export > EDF
    * A small pop-up named 'Export EDF' will appear
2. Select all of the EEG/EMG channels used in the experiment
    * If you ran more than one mouse in a project/experiment, verify which EEG/EMG channels correspond to which mouse. You may choose to export only the EEG/EMG channels corresponding to each mouse into separate files
3. In the 'Filename' prompt, choose the desired folder destination
4. Set the date/time range you would like to export in the 'Start Time' and 'End Time' prompts (format: MM/DD/YEAR HH:MM:SS.00)
4. Click 'OK'

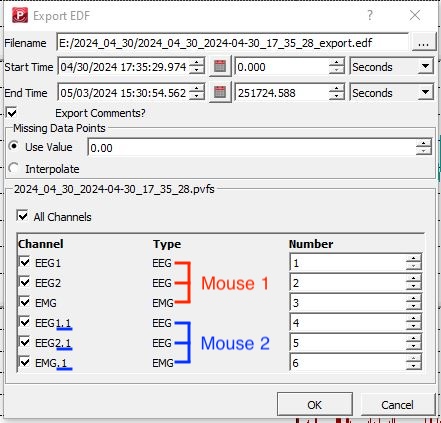
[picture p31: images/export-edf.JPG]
Export EDF pop-up window


**Figure 1:** _A pop-up window named 'Export EDF' will appear after selecting the 'File > Export > EDF' option in the top toolbar. Note how the EEG/EMG channel names of one amplifier are distinguished from another amplifier (e.g. EEG1 vs. EEG1.1, EMG vs. EMG.1, etc.)_

[← Return to setup guide](../readme.md#setup-guide)

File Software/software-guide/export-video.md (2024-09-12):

## Exporting video

This portion of the guide explains how to export video from the EEG/EMG sleep recording projects.

Using Sirenia Acquisition, we first export video files in the `.webm` format, each of which are up to 24 hours long. Then, we use `ffmpeg` and a Windows PowerShell script to slice and convert these '.webm' files to sequential, hour-long '.mp4' video files. These videos can be used to track the XY movement of mice and serve as an aid for sleep state scoring.

**Software required**
- [Sirenia Acquisition](https://www.pinnaclet.com/sirenia-download.html)
- [ffmpeg](https://www.gyan.dev/ffmpeg/builds/)
- ['webm-splitter.ps1' Windows PowerShell script](../scripts/webm-splitter.ps1)
- Windows OS

### Guide

1. [Export video in Sirenia Acquisition](#export-video-in-sirenia-acquisition)
2. [Install ffmpeg](#install-ffmpeg)
3. [Slice and convert videos](#slice-and-convert-videos)

### Export video in Sirenia Acquisition

1. In the top toolbar, select 'File > Export > Video'
    * A small pop-up named 'Export Video' will appear
2. In the 'File' prompt, choose the desired folder destination and filename
    * It's recommended to export all videos corresponding to each mouse into separate folders
3. Set the date/time range you would like to export in the 'Start Time' and 'End Time' prompts (format: MM/DD/YEAR HH:MM:SS.00)
    * **Video duration should be no longer than 24 hours (24:00:00)**
4. Select the `.webm` file extension
5. Select the desired camera video source (select only one source per video export)
6. Click 'OK'
    * A new 'Exporting Video' window will appear with a green progress bar
7. Once complete, a new window will pop up asking: 'Optimize webm file?'
    * Click 'Yes'
  
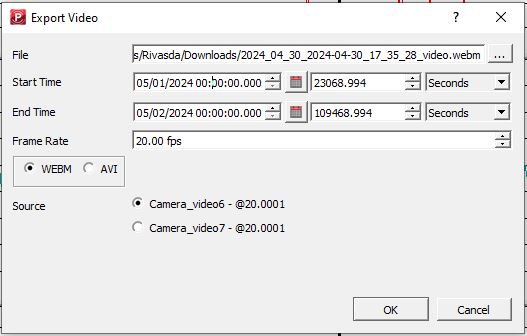
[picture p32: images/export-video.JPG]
Export Video pop-up window
  
  
  **Figure 1:** _A pop-up window named 'Export Video' will appear after selecting the 'File > Export > Video' option in the top toolbar._

### Install ffmpeg

This portion of the guide explains how to install `ffmpeg`, which is used to split and convert `.webm` videos to `.mp4`.

1. Download the lastest ffmpeg essentials build for Windows OS [here](https://www.gyan.dev/ffmpeg/builds/)
2. Extract the folder to the `C:` local disk drive
3. Right click the Windows Start Menu icon in the lower left taskbar, then select 'System'

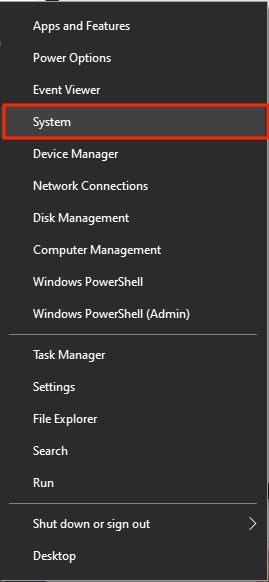
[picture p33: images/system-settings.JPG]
Windows System Settings


**Figure 2:** _Access the System Settings by right clicking the Windows Start Menu icon and selecting 'System'._

4. Click on 'Advanced system settings'
5. A new 'System Properties' window will appear. Click 'Environment Variables...'
6. Under 'System variables' highlight the 'Path' variable and click 'Edit'

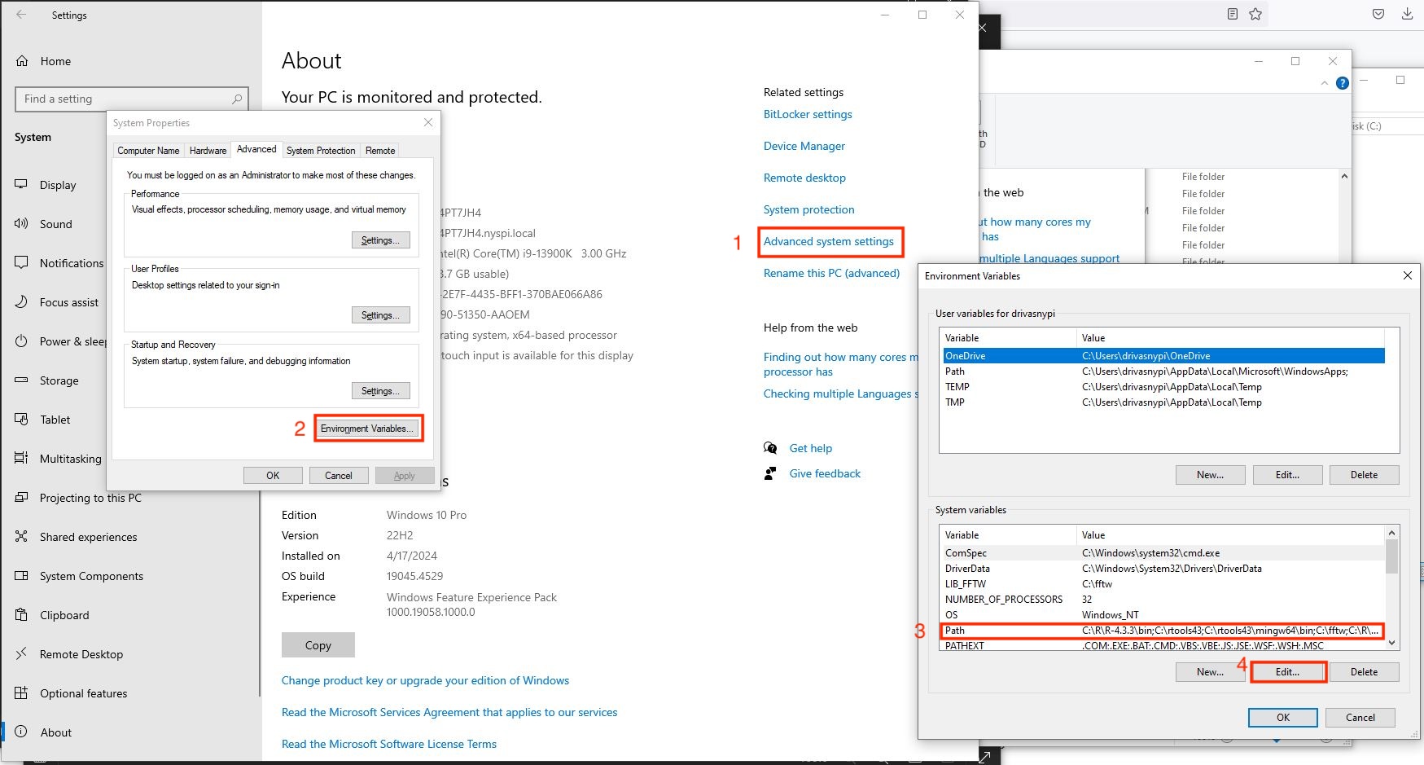
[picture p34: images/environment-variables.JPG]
Windows Environment Variables


**Figure 3:** _Click 'Advanced system settings' (1), then click 'Environment Variables...' (2). In the 'Environment Variables' window, highlight 'Path' (3), then click 'Edit' (4)._

7. A new 'Edit environment variable' window will open
    * Click 'New', then paste the ffmpeg `bin` directory address (e.g. `C:\ffmpeg-7.0.1-essentials_build\bin`)
    * Click 'OK'

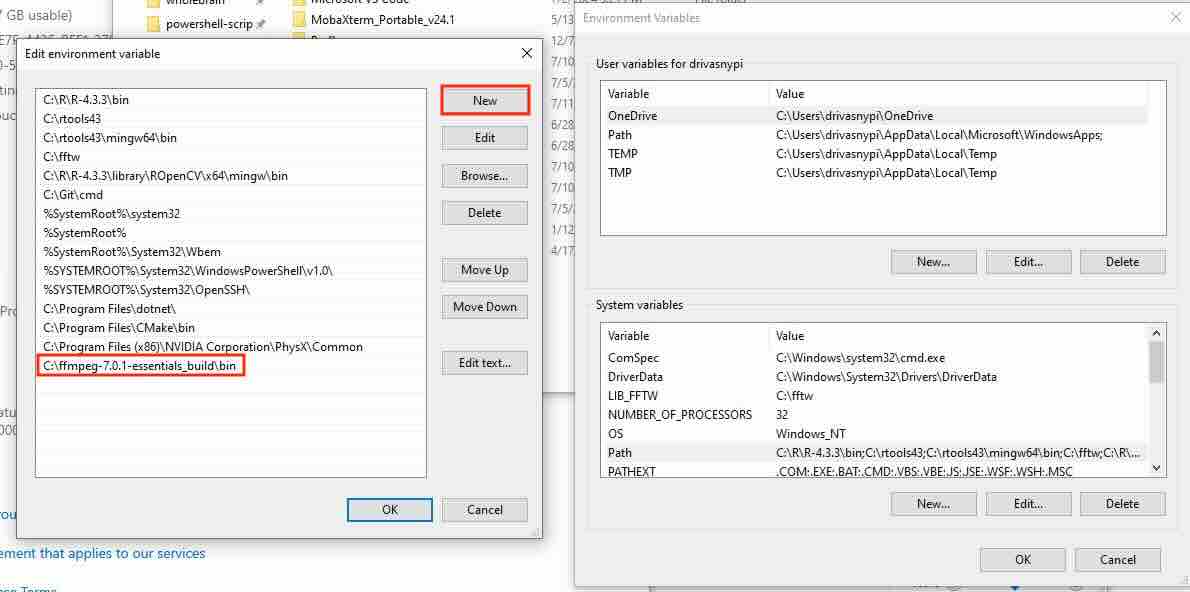
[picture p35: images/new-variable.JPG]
Creating a new Windows PATH Environment Variable


**Figure 4:** _In the 'Edit environment variable' window, click 'New', then paste the ffmpeg `bin` directory address._

8. To test if ffmpeg was installed successfully, launch the 'Command Prompt' and execute the command `ffmpeg`
    * The terminal should output the ffmpeg version, build, and configuration

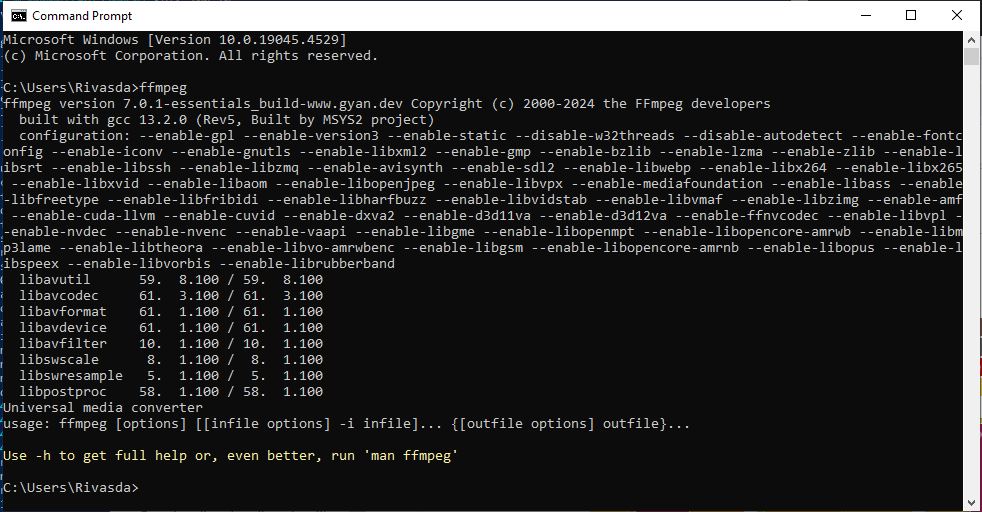
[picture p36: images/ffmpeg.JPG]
Verifying ffmpeg installation


**Figure 5:** _In the 'Command Prompt', run the `ffmpeg` command to see an output similar to this figure._

### Slice and convert videos

This portion of the guide explains how to slice and convert multi-hour long '.webm' videos to sequential, 1-hour long videos ('.mp4' format)

1. Download the `webm-splitter.ps1` Windows PowerShell script [here](.././scripts/webm-splitter.ps1)
2. Open Windows PowerShell
3. In the terminal, change the current directory to the folder where the script was installed using the `cd` command (e.g. `cd C:\Users\Rivasda\Documents\powershell-script`)
4. Request authority to run the script by running this command: `Set-ExecutionPolicy -Scope Process -ExecutionPolicy Bypass`
    * A prompt for the 'Execution Policy Change' will appear
    * Enter `Y` 
5. Finally, run the script using this command: `.\webm-splitter.ps1`
6. When prompted, paste and enter the folder path containing the '.webm' files (e.g. `C:\Users\Rivasda\Downloads\2024_04_30`)
    * Within the folder path, the script will create a subfolder for each '.webm' file. The output videos will be saved to the corresponding subfolder (named after the source video file)

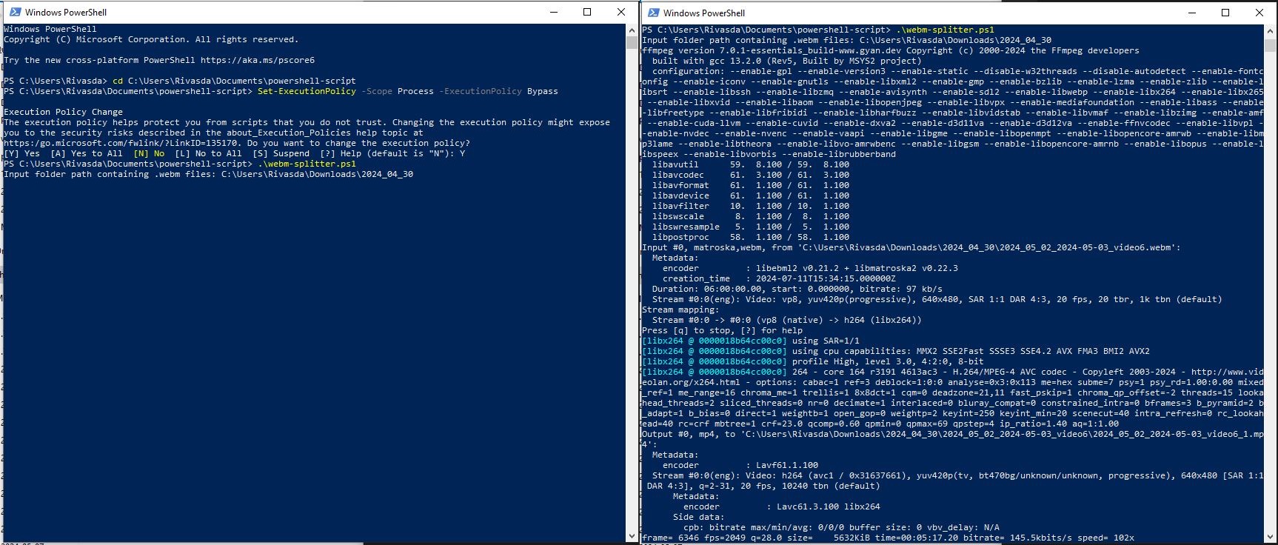
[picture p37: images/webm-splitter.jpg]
Running the Windows PowerShell webm-splitter script


**Figure 6:** _An example of the user input to run the `webm-splitter.ps1` script (left window) and the resulting output while it's running (right window)._

7. Check the video outputs and ensure the files are not corrupt

[← Return to setup guide](../readme.md#setup-guide)

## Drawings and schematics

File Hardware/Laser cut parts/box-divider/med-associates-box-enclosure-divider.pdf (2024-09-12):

2
1

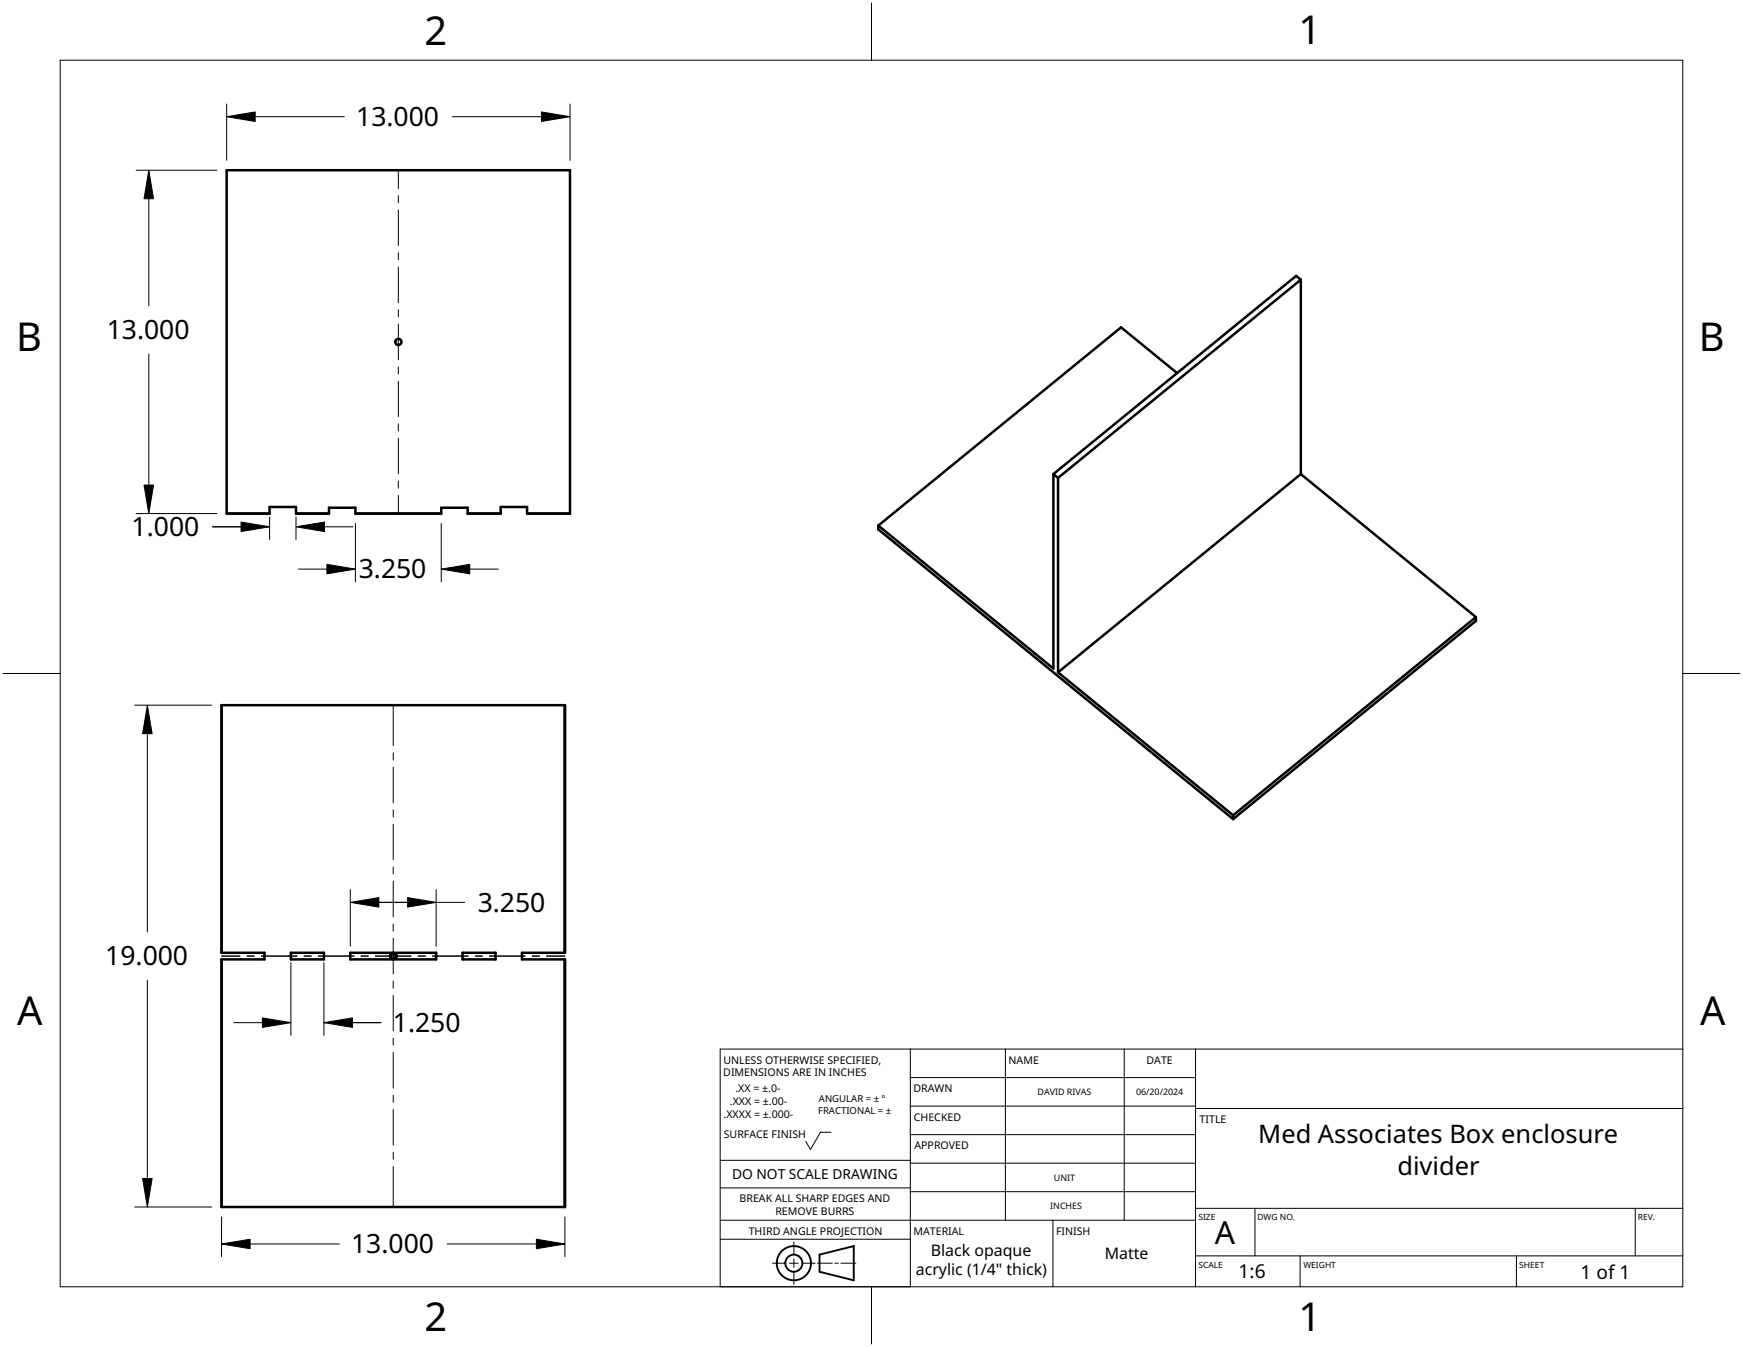
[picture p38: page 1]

UNLESS OTHERWISE SPECIFIED, DIMENSIONS ARE IN INCHES .XX = ±.0-.XXX = ±.00-ANGULAR = ± ° .XXXX = ±.000-FRACTIONAL = ± SURFACE FINISH | | NAME | DATE

DRAWN | DAVID RIVAS | 06/20/2024

CHECKED | | | TITLE Med Associates Box enclosure divider

APPROVED

DO NOT SCALE DRAWING | | UNIT

BREAK ALL SHARP EDGES AND REMOVE BURRS | | INCHES

SIZE A | DWG NO. | REV.

THIRD ANGLE PROJECTION | MATERIAL Black opaque acrylic (1/4" thick) | FINISH Matte

SCALE 1:6 | WEIGHT | SHEET 1 of 1

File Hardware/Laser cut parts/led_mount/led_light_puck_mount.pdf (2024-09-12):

2
1

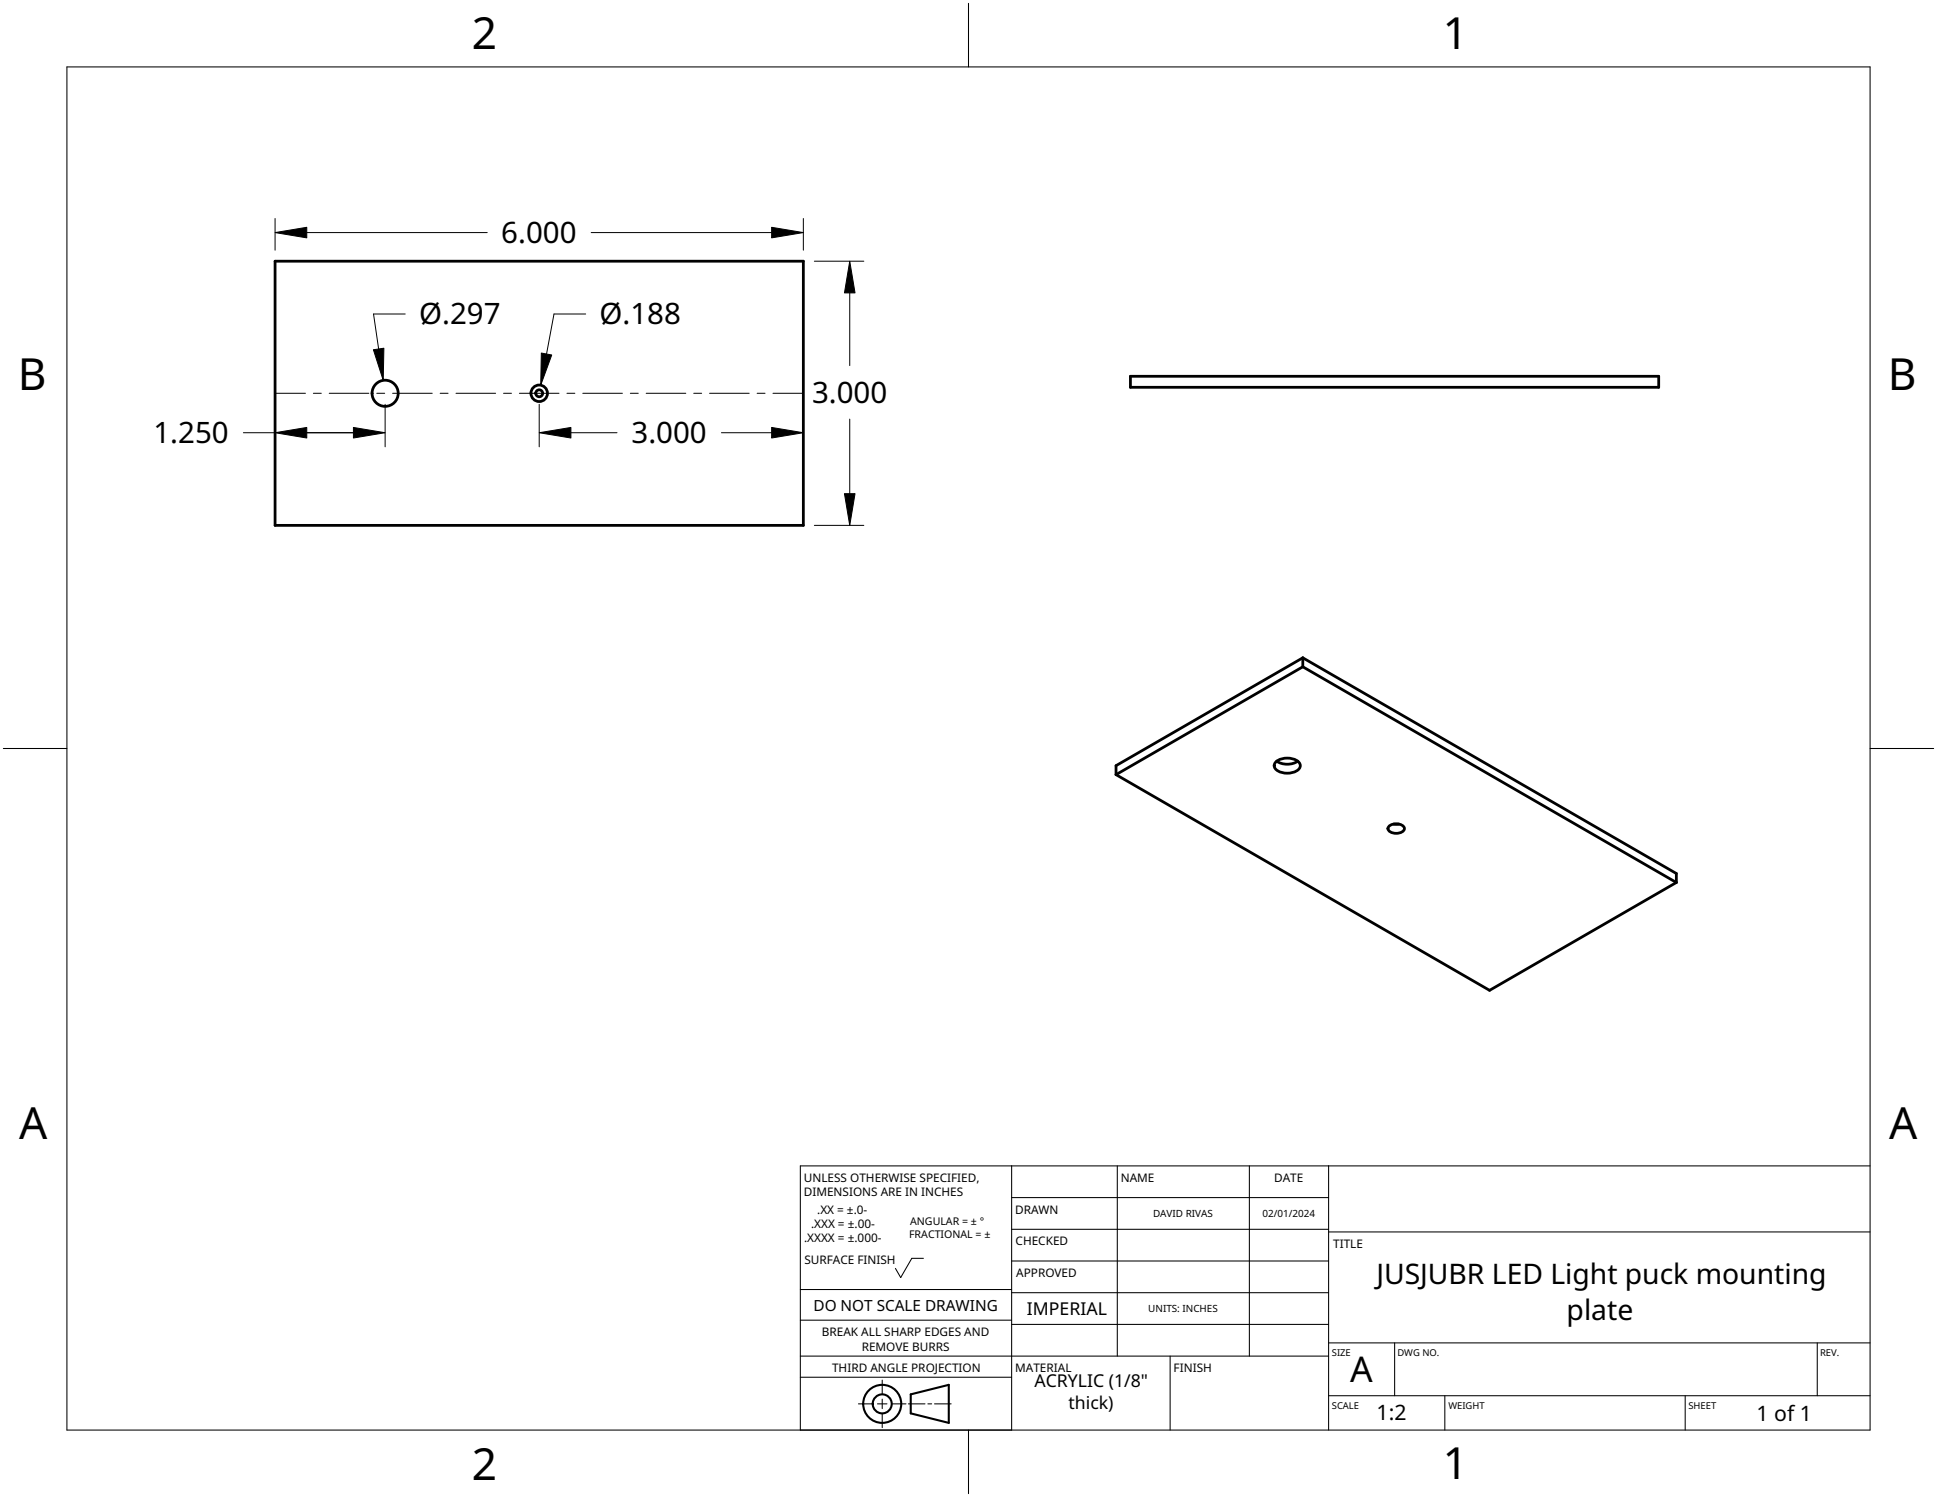
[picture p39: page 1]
MATERIAL ACRYLIC (1/8" thick); FINISH

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

DRAWN | DAVID RIVAS | 02/01/2024

CHECKED | | | TITLE JUSJUBR LED Light puck mounting plate

APPROVED

DO NOT SCALE DRAWING | IMPERIAL | UNITS: INCHES

BREAK ALL SHARP EDGES AND

REMOVE BURRS
THIRD ANGLE PROJECTION

SIZE A | DWG NO. | REV.

SCALE 1:2 | WEIGHT | SHEET 1 of 1

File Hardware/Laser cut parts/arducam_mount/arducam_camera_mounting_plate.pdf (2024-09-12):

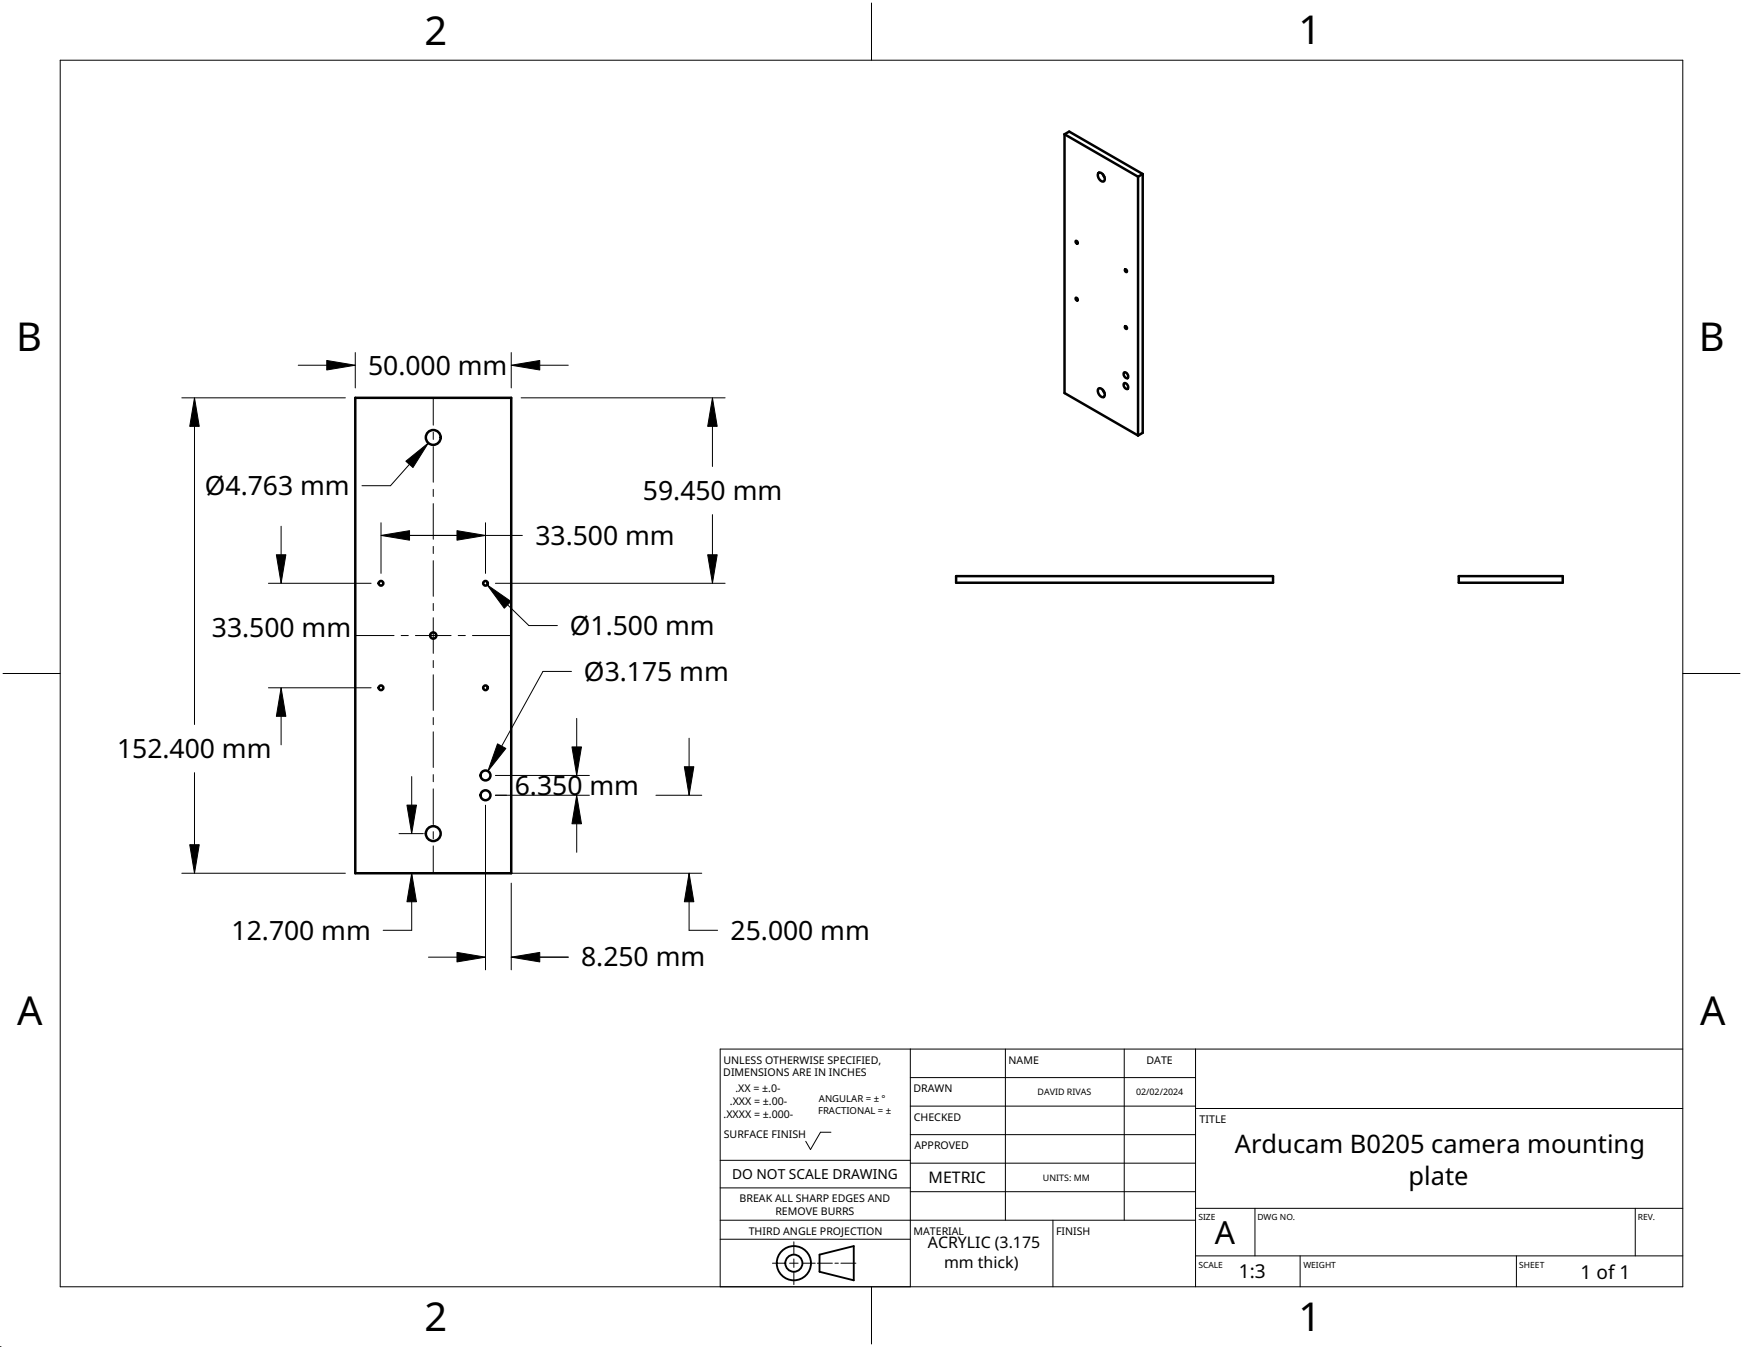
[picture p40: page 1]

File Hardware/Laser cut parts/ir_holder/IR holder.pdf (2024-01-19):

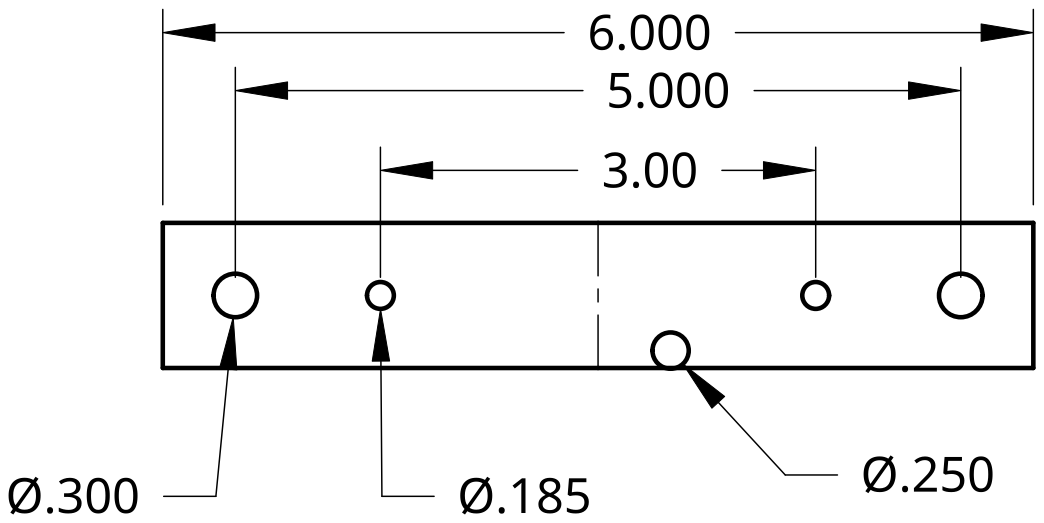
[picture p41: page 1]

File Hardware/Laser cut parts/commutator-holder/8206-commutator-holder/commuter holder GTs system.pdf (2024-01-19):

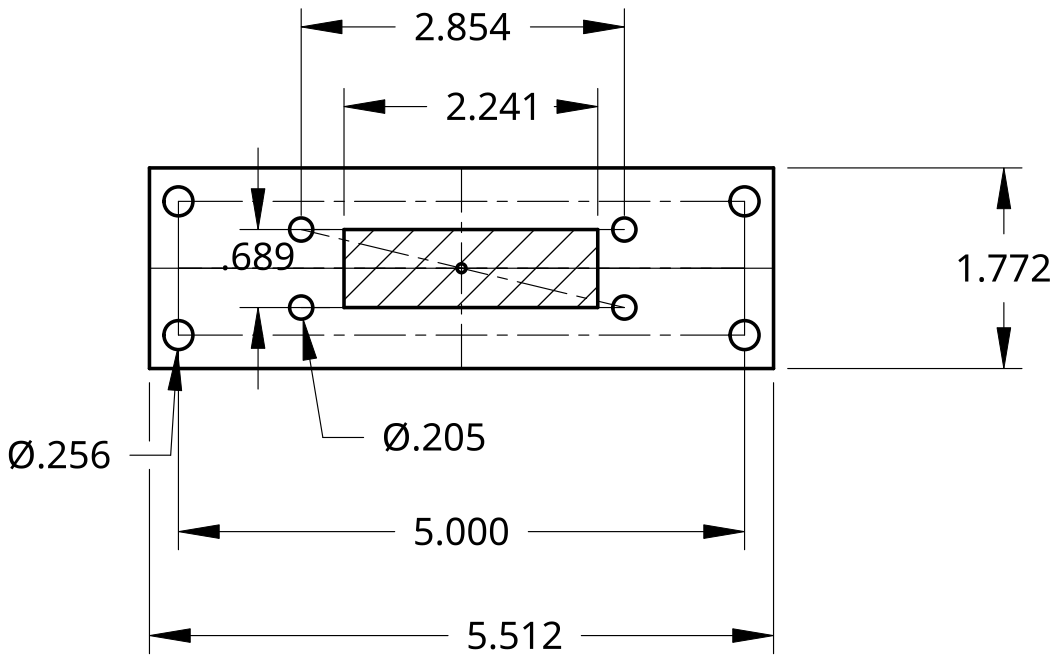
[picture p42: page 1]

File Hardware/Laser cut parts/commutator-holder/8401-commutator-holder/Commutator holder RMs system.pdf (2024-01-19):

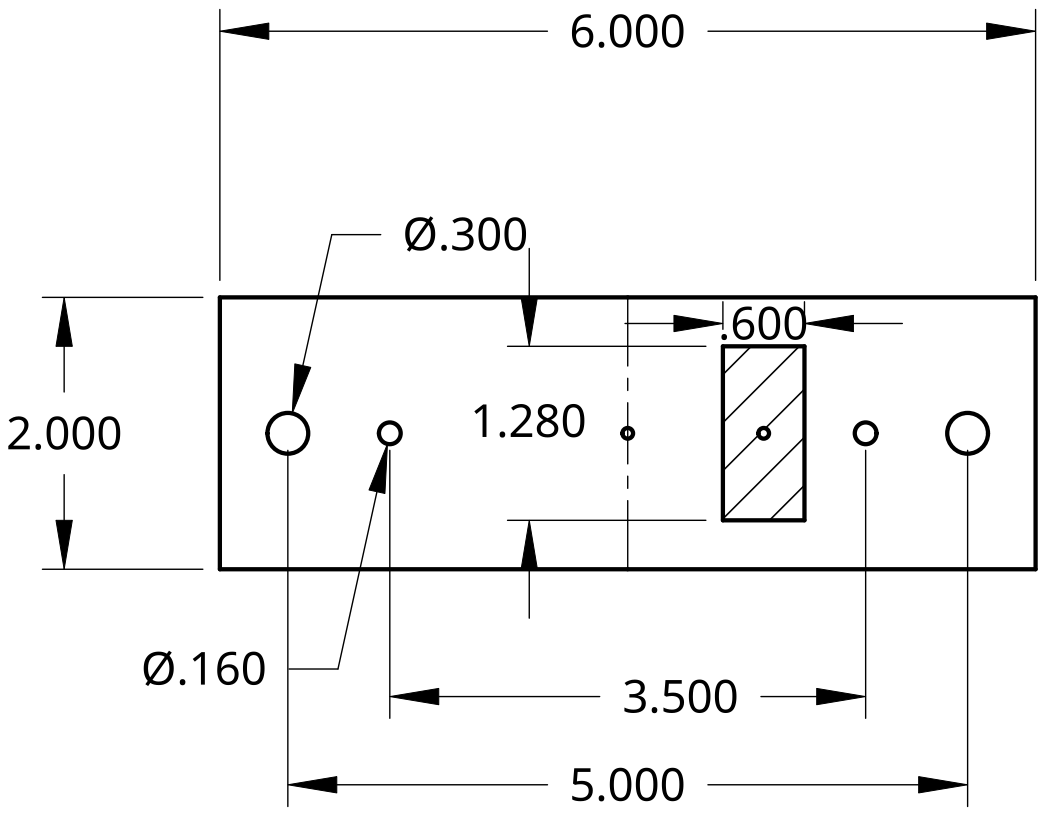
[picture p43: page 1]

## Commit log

2024-01-19 bluprints for hardware components
    [Commuter holder RMs system.dxf, IR_holder.dxf, commuter holder GTs system.dxf]
2024-01-20 Add link to laser-cut-parts
2024-01-20 Remove link to laster-cut-parts
2024-02-03 Add arducam laser-cut files
    [arducam_camera_mounting_plate.dxf]
2024-02-03 Add LED light laser-cut files
    [led_light_puck_mount.dxf]
2024-02-03 Move commutator files to commutator-holder
    [Commuter holder RMs system.dxf, commuter holder GTs system.dxf]
2024-02-03 Move IR holder files to ir_holder
    [IR_holder.dxf]
2024-02-03 Move LED mount files to led_mount
    [led_light_puck_mount.dxf]
2024-02-03 Move arducam mount files to arducam_mount
    [arducam_camera_mounting_plate.dxf]
2024-02-03 Add link to 6-pin cable
2024-02-03 Add recording enclosure to hardware requirement
2024-02-03 Move 8401 commutator files to 8401-commutator-holder
    [Commuter holder RMs system.dxf]
2024-02-03 Move 8206 commutator files to 8206-commutator-holder
    [commuter holder GTs system.dxf]
2024-02-03 Add camera setup guide
2024-02-03 Add recording enclosure setup
2024-02-03 Add recording enclosure materials
2024-02-03 Add logitech-ir-filter.jpg
2024-02-03 Add recording-enclosure.jpg
2024-02-04 Crop logitech-filter.jpg
2024-02-04 Update recording enclosure guide
2024-02-04 Fix list nesting in recording enclosure guide
2024-02-04 Change width of recording-enclosure.jpg
2024-02-04 Remove duplicate text from recording enclosure guide
2024-02-04 Add LED rotary dimmer switch
2024-02-12 Add wiring duct
2024-02-13 Add camera-setup guide
2024-02-13 Add recording-enclosure guide
2024-02-13 Fix laser cut file path
2024-02-13 Fix laser-cut file path
2024-02-13 Add plate-mounts.jpg
2024-02-13 Add led-mounting-plates.jpg
2024-02-13 Add figures and detail mounting plate install
2024-02-13 Add cable-management.jpg
2024-02-13 Add wiring-duct.jpg to images
2024-02-13 Add cable-management guide
2024-02-13 Add cable management to setup guide
2024-02-13 Update note for wiring duct
2024-02-13 Update cable-management guide
2024-02-13 Update T-nut cat#
2024-02-13 Update steps and T-nut cat#
2024-06-11 Remove logitech setup from camera guide
2024-06-11 Update acrylic material
2024-06-20 Add box divider laser-cut files
    [box-divider-pt1.dxf, box-divider-pt2.dxf]
2024-06-20 Edit material thickness
2024-06-25 Add fan-cover laser-cut files
    [fan-cover-pt1.dxf, fan-cover-pt2.dxf, fan-cover-pt3.dxf, fan-cover-pt4.dxf]
2024-06-25 Edit materials, update fan-cover guide
2024-06-25 Update acrylic materials
2024-07-12 Rename powershell script
2024-07-13 Fix typo in Bill of Materials header
2024-07-14 Fix typo in powershell script guide
2024-09-12 Add recording enclosure files for laser cutting
